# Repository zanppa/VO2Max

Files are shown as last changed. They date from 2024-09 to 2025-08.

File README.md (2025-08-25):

# Vo2max
A portable and affordable DIY [spirometer](https://en.wikipedia.org/wiki/Spirometer) project to measure [VO2 Max](https://en.wikipedia.org/wiki/VO2_max) during an excercise. This is still a prototype and heavily in development.

This project turned out to be a complete rewrite and redesign of [Ivor Hewitt's VO2max](https://github.com/ihewitt/VO2max) spirometer project, which in turn was based on [Rabbitcreek's project](https://www.instructables.com/Accurate-VO2-Max-for-Zwift-and-Strava/).

The main idea was to have a fully 3D printable system, but printing the mask part turned out to be difficult so the current version uses parts from a commercial (but affordable) mask. There are plans to develop a model that can be 3D printed with soft material (TPU/TPE).

Current features:
 - [X] Exhalation volume measurement (with calibration function)
 - [X] Exhalation oxygen level measurement (with calibration function)
 - [X] VE and VO2(max) calculations
 - [X] Ambient pressure and temperature measurement for reducing measurements to STDP 
 - [X] Bluetooth LE heart rate sensor support
 - [X] Streaming data over WiFi to computer
 - [X] PC companion program to monitor and record the WiFi stream
 - [X] Recording values to memory buffer (1024 samples, at 15 s calculation interval over 4 hours)
 - [X] Storing recorded values to a file (single file in flash, retained over power off)
 - [X] PC tool to read and store the recorded values
 - [ ] Bluetooth [Golden Cheetah](https://www.goldencheetah.org/) support as VO2 Master (based on Ihewitt's code)
 
Main architectural changes in the code:
 - Restructured to use FreeRTOS tasks
 - Time-accurate sampling of sensors, e.g. air flow is measured every 20 ms
 - Lower priority tasks like bluetooth, wifi and display do not interrupt sensor reading
 - Code is divided to "sub modules" for easier upkeep
 
## Usage
This VO2Max measurement device is designed to have two operation modes:

1. Stand-alone use. In this mode the device is used independently and handles all calculations internally. Values can be monitored from the device's display, and the data is stored to memory (and optionally to flash memory). The stored values can later be transferred to a computer via WiFi.
2. Real-time monitoring mode. In this mode a computer is connected to the device via WiFi and all measured quantities are transferred to the computer in real time. The computer can record the values and/or do the calculations (of course, also the VO2Max's calculated values are transferred).

For detailed usage info see [how-to-use.md](how-to-use.md).

## Hardware
This is a listing of the hardware that is used and supported by the code and 3D models. Some of the hardware were different from the reference projects for availability reasons in the EU, or due to technical reasons like mounting.

 - A rubber (silicone?) half face dust mask with detachable parts, see links/pictures below
 - [LilyGo T-Display](https://www.lilygo.cc/products/lilygo%C2%AE-ttgo-t-display-1-14-inch-lcd-esp32-control-board) ESP32 development board with 1.14" display
 - [DFRobot SEN0322](https://www.dfrobot.com/product-2052.html) Gravity: Electrochemical Oxygen sensor (0-25% Vol, I2C)
 - [Sensirion SDP801](https://sensirion.com/products/catalog/SDP801-500Pa/) Digital +/-500Pa differential pressure sensor, I2C, manifold connection
 - [Bosch BMP388](https://www.bosch-sensortec.com/products/environmental-sensors/pressure-sensors/bmp388/) ambient pressure sensor (e.g. [DFRobot SEN0251 Gravity: BMP388](https://www.dfrobot.com/product-1792.html))
 - Thread forming 2.5x8mm screws (6 pcs) (e.g. [Bossard 3034065](https://www.bossard.com/eshop/global-en/direct-assembly-screws/direct-assembly-screws-for-plastics/ecosyn-plast/p/82428/?category=01.200.300&index=7)) and 2.5x16mm screws (2 pcs) (e.g. [Bossard 3034077](https://www.bossard.com/eshop/global-en/direct-assembly-screws/direct-assembly-screws-for-plastics/ecosyn-plast/p/82428/?category=01.200.300&index=7))
 - 14500 size Lithium-ion battery and suitable connection parts (spring terminals or similar)
 - 2 pcs of 4.5 x 1.5 mm O-rings
 
## Where to buy
Most of the necessary electronics components were bought from [Mouser](https://eu.mouser.com/).

The display and half mask was bought from [Aliexpress](https://www.aliexpress.com). Many stores had similar masks so a random, somewhat professional looking one was selected and the mask that was received was ok. Prepare for a long delivery time, 6 weeks or so.

Links to the main components that were used are below with their price at the time of building (incl. VAT etc.).

| Component | Source | Price |
| --------- | ------ | ----- |
| DFRobot Sen0322 | [Mouser](https://eu.mouser.com/ProductDetail/DFRobot/SEN0322?qs=sPbYRqrBIVnCRTCgFw%2FJyQ%3D%3D) | 50.13 € |
| Sensirion SDP801 | [Mouser](https://eu.mouser.com/ProductDetail/Sensirion/SDP801-500Pa?qs=PzGy0jfpSMsYh%2Fiz3%252Braew%3D%3D) | 30.50 € |
| DFRobot SEN0251 BMP388 | [Mouser](https://eu.mouser.com/ProductDetail/DFRobot/SEN0251?qs=sGAEpiMZZMsvmS05OVPORkos2oZHucfRYva4AowfgwtRmiD%2F%252BmISIg%3D%3D) | 6.42 € |
| Lilygo T-Display 16MB CH9102F | [Aliexpress lilygo Official store](https://www.aliexpress.com/item/33048962331.html) | 16.18 € |
| Dustproof half-mask | [Aliepress CKE-Labour Pro Store](https://www.aliexpress.com/item/1005005820042955.html) | $ 6.24 |

# Assembly

## Valve assembly
Exhalation and inhalation valves are required. Valve itself consists of two 3D printed parts (body and membrane holder), membrane template and the membrane itself. In addition, inhalation valve needs a counterpart for mounting. Current design uses two different sizes of valves due to how the commercial mask was built.

 1. Print all the valve parts
 2. Using the template, cut the membrane from suitable material. Rubber glove can be used as the membrane. One may experiment with different materials
 3. Insert the membrane into the valve body
 4. Place the membrane holder on the membrane. Carefully push the ends of the holder slightly and rotate the holder into the clips. Take care to ensure that the membrane is still centered and has no wrinkles
 
## I2C distribution board
A simple I2C distribution board is needed to be mounted on top of the Sensirion SDP801 sensor. This also helps in mounting the sensor.

Mill or etch and drill or order the board, and then solder the sensor wires to them. I recommend measuring the wires yourself but the lengths of the wires are roughly:
 - 20 cm for the oxygen sensor
 - 16 cm for the ambient pressure sensor
 - TBD cm for the display/processor
 
I recommend routing one sensor wire from the backside and other wires from the front.

Also solder 1.3 kOhm pull-up resistors between VDD and SDA and SCL.

Finally the Sensirion SDP801 can be soldered to the distribution board.

## Main body assembly
Main body consists of a single 3D-printed main part. Support is needed at the bottom parts and about 6 mm outer brim should be used to ensure that the part stays upright. With a bed-slinger printer, orient the print so that the wide side is parallel to the moving axis.

 1. Print the body and remove all support material
 2. Mount the oxygen sensor on top with 4x 2.5x8mm screws
 3. Mount the ambient pressure/temperature sensor on the side with 2x 8mm screws
 4. Place the O-rings on the recesses of the pressure sensor location
 5. Mount the SDP801 pressure sensor with 2x 2.5x16mm screws
 6. Wire the battery terminals to the T-display battery connector
 7. Install the battery terminals and connect the connector to T-display
 6. Place the display on the front of the unit
 7. Carefully measure cables, cut and solder them, removing parts from the body if necessary during soldering
 8. Use 1.3 kOhm external pull-up resistors for I2C SDA and SCL (preferably soldered to the I2C distribution board)

Note that the battery terminals nor the power switch are currently included in the model. One should find suitable parts for this and glue them in place.

The battery holder might be a bit tight, so some sanding/cutting of the edges may be necessary.
 
## Flashing the firmware
The firmware was built with PlatformIO v core 6.1.18, home 3.4.4. One needs to install lilygo-t-display board (or it may get installed automatically when building...)

Following external libraries are needed:

 - TFT_eSPI (version 2.5.34)
 - NimBLE-Arduino for Bluetooth LE (version 1.4.1)
 
Other drivers are included in the repository with necessary modifications.

To build the software select following as the board settings:

 * Board: Lilygo-t-display
 * Upload Speed: 921600
 * CPU Frequency: 240Mhz (WiFi/BT)
 * Flash Frequency: 80Mhz
 * Flash Mode: QIO
 * Partition Scheme: Default.csv [4MB with spiffs (1.2MB APP/1.5 SPIFFS)]
 * Core Debug Level: None --> For debugging can set also different values, for release select None
 * PSRAM: No

# Disclaimer
This is not a medical device! Use at your own responsibility.

This repository contains code, models and similar for educational purposes only and are supposed 
to be used for reference. Everything is provided as is, without any warranty. The author is not 
liable for any damages or other liability arising from use of anything provided here.

# Copyright
Copyright 2024, 2025 Lauri Peltonen

Licensed under GPLv3.

Drivers included in this repository may have their own licenses which are included in the relevant 
source files.

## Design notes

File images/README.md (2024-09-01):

This directory contains images and pictures of the VO2Max device

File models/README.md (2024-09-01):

This directory contains the 3D models that need to be 3D printed.

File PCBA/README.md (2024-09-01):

# Sensirion SDP801 PCBA
This directory contains the simple PCBA to be mounted on top of the Sensirion SDP801 
pressure sensor. It also functions as a I2C distribution board.

Gerbers are provided for reference, as the board is very simple and was drawn 
by hand.

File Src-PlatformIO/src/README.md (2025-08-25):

# Source code for VO2Max project
This directory contains the source code for the VO2Max project.

Source code is written for ESP32 with PlatformIO (Core 6.1.18, Home 3.4.4).

## PlatformIO board settings
The settings are defined in ```platformio.ini``` but the key values are listed here also.

 * Board: Lilygo-t-display
 * Upload Speed: 921600
 * CPU Frequency: 240Mhz (WiFi/BT)
 * Flash Frequency: 80Mhz
 * Flash Mode: QIO
 * Partition Scheme: Default.csv [4MB with spiffs (1.2MB APP/1.5 SPIFFS)]
 * Core Debug Level: None --> For debugging can set also different values, for release select None
 * PSRAM: No

## External library requrirements
 * TFT_eSPI (tested with version 2.5.34)
 * NimBLE_Arduino (tested with version 1.4.1)

## Other stuff
Remember to modify the TFT_eSPI configuration file to select T-Display! File should be located in ```.pio/libdeps/lilygo-t-display/TFT_eSPI/User_Setup_Select.h```. The correct line to uncomment is 
```
#include <User_Setups/Setup25_TTGO_T_Display.h>    // Setup file for ESP32 and TTGO T-Display ST7789V SPI bus TFT
```

Don't forget to comment out the default custom ```User_Setup.h``` configuration file
```
//#include <User_Setup.h>           // Default setup is root library folder
```

With NimBLE-Arduino the code just barely fits into default partition (1.25 MB App, 1.375 MB SPIFFS).

It would be possible to change to huge_app (3 MB app, 0.875 MB SPIFFS) if more application space is needed.

## Library requirements
### External
 * TFT_eSPI @ 2.5.43
 * NimBLE-Arduino @ 1.4.1

### Built into ESP32 platform
 * EEPROM @ 2.0.0
 * ESP32 Async UDP @ 2.0.0
 * WiFi @ 2.0.0

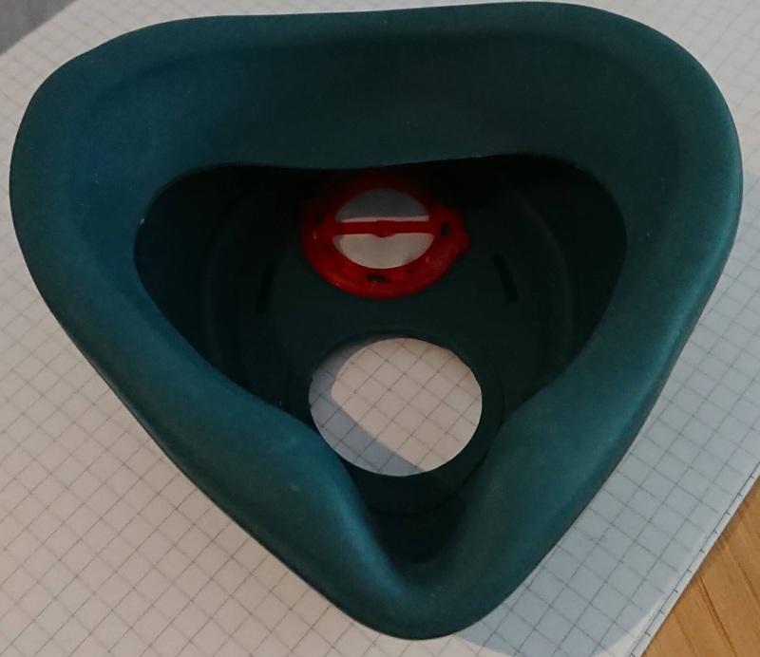
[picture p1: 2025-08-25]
images/inlet_3.jpg

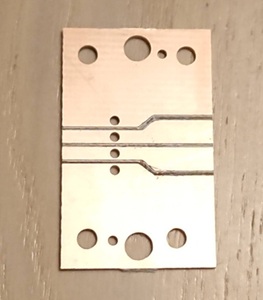
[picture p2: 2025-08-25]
images/i2c_board_1.jpg

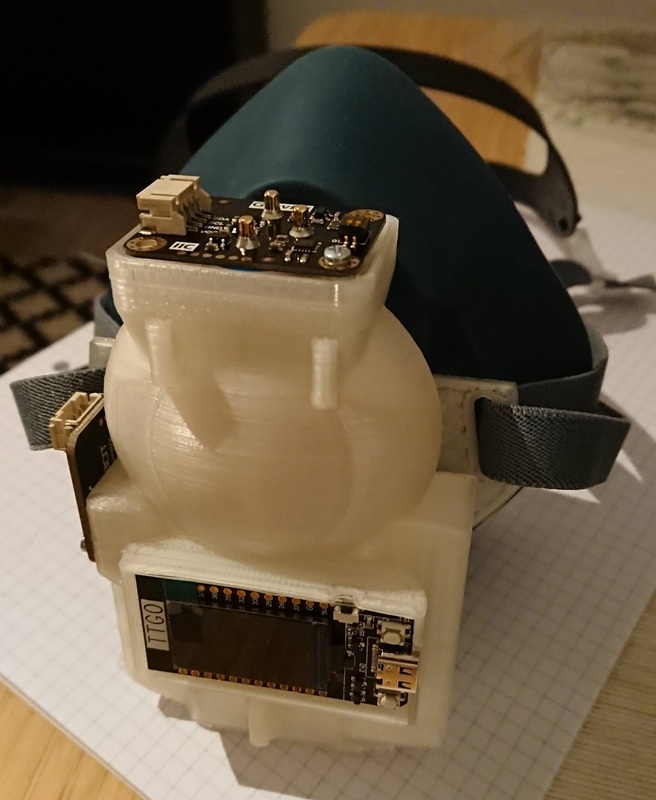
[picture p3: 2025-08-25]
images/boards_1.jpg

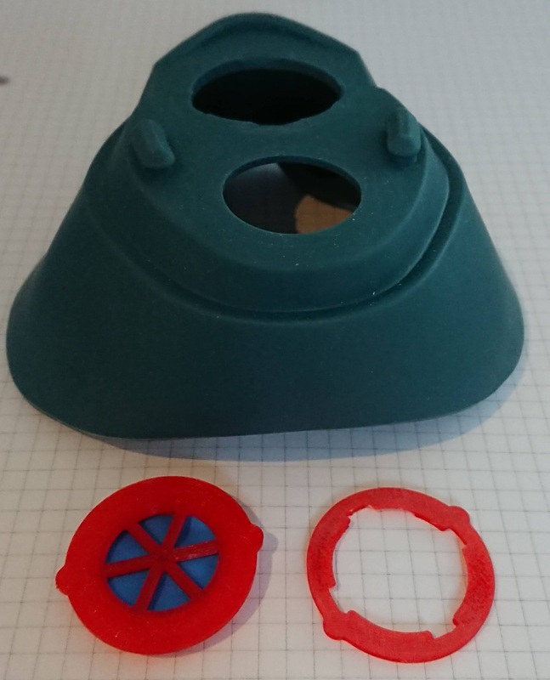
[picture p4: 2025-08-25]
images/inlet_1.jpg

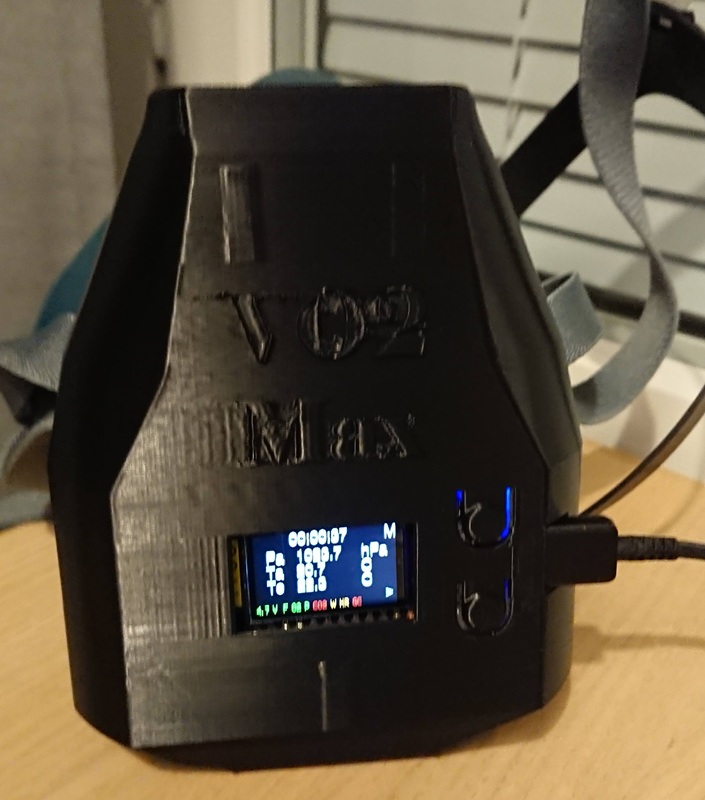
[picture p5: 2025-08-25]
images/cover_1.jpg

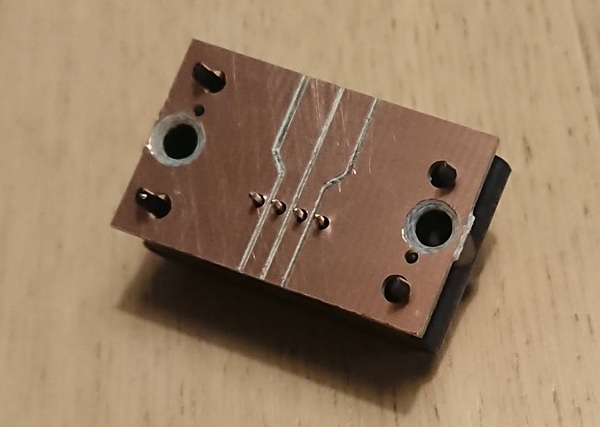
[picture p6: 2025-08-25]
images/i2c_board_2.jpg

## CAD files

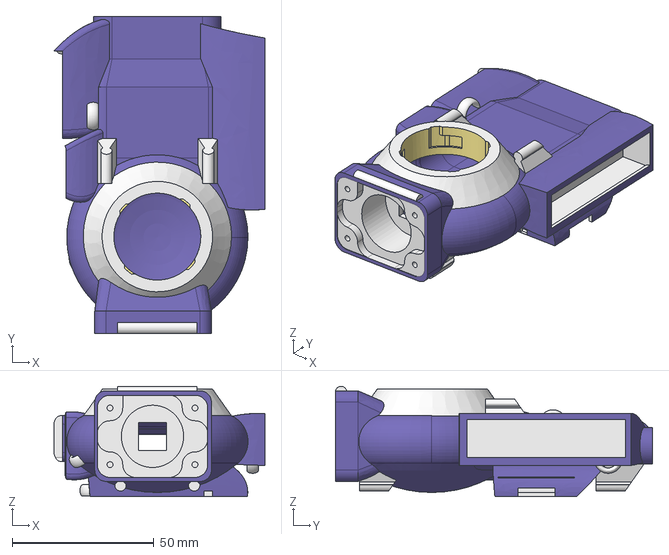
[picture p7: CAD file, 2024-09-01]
models/Main model v12.step
74.5 x 112.0 x 39.0 mm

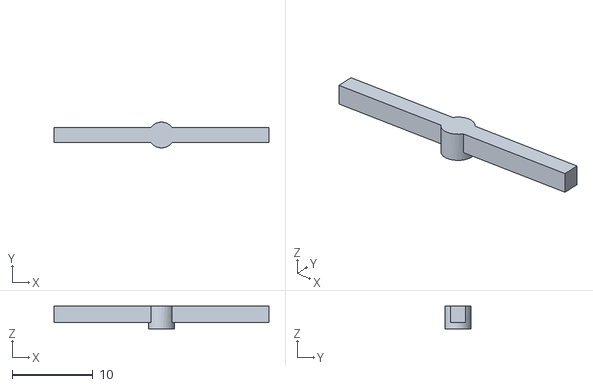
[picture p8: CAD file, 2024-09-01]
models/Outlet valve v2 30mm membrane holder.stl
26.6 x 3.20 x 2.80

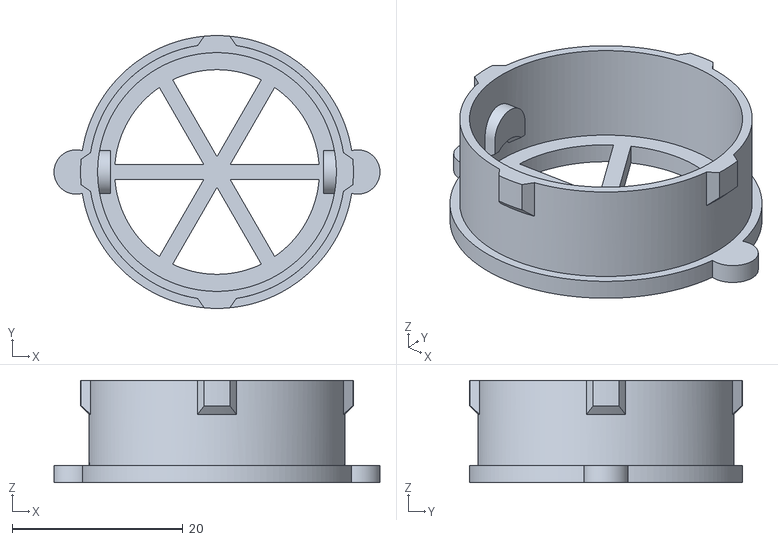
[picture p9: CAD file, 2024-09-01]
models/Outlet valve v2 30mm body.stl
38.2 x 32.0 x 12.0

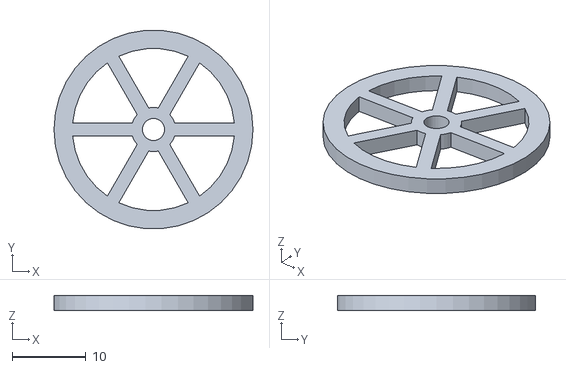
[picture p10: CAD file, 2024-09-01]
models/Outlet valve v1 30mm template.stl
27.0 x 26.9 x 2.00

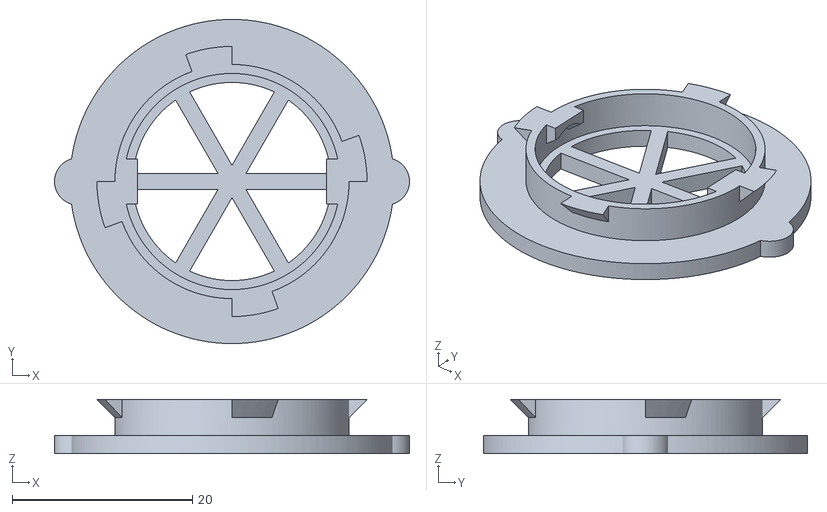
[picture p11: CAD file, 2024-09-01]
models/Inlet valve v4 26mm body.stl
39.4 x 36.0 x 6.00

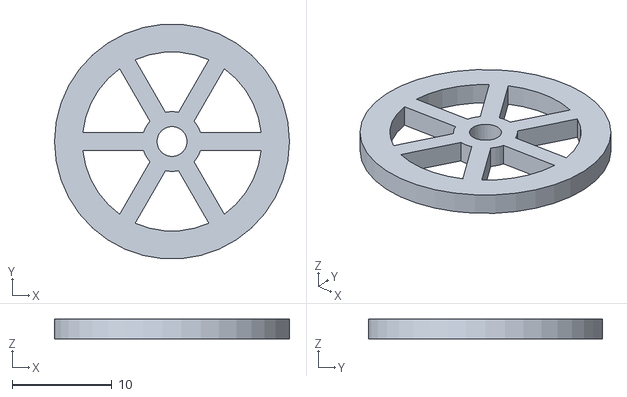
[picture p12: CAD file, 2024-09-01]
models/Inlet valve v3 26mm template.stl
23.6 x 23.5 x 2.00

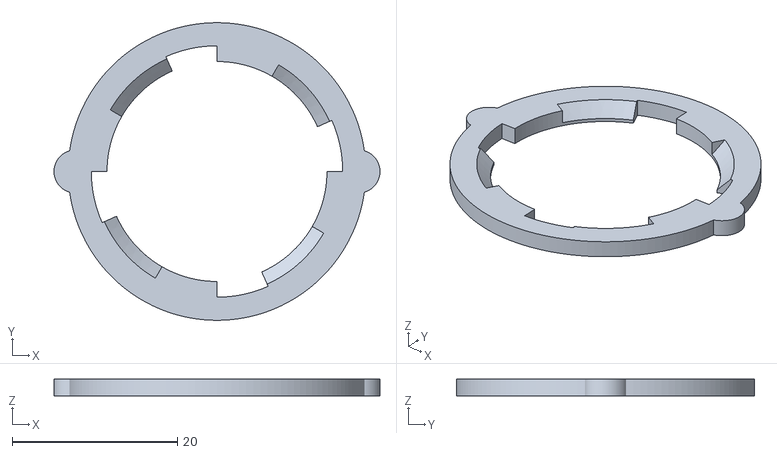
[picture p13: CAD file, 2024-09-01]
models/Inlet valve v4 26mm retainer.stl
39.4 x 36.0 x 2.00

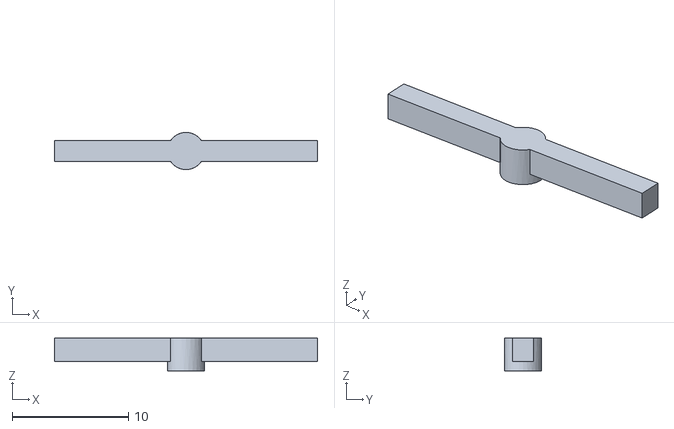
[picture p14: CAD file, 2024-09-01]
models/Inlet valve v3 26mm membrane holder.stl
22.6 x 3.20 x 2.80

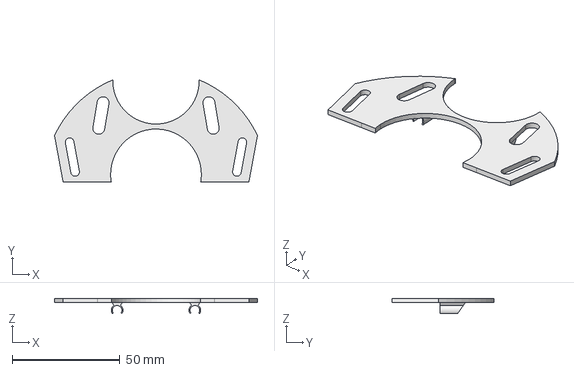
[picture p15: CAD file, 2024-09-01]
models/Mask holder v10.step
94.0 x 47.4 x 7.05 mm

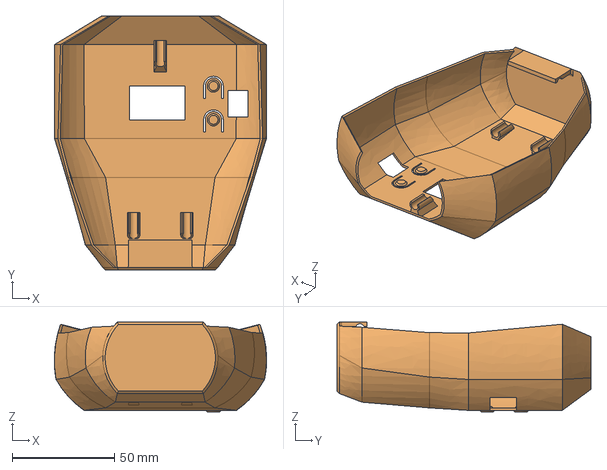
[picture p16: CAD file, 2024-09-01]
models/Cover v12.step
103.8 x 124.2 x 44.0 mm

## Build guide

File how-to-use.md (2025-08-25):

# How to use VO2Max
This document describes basic usage of the VO2Max portable spirometer.

## Getting started

The device is powered on either by plugging in USB-C cable or by connecting a Li-Ion battery to the T-Display board.

After power on, the oxygen sensor requires 3 minutes of warm-up for measurement to be stable and accurate. A timer will be shown on the display counting down from 180 every second and displaying the oxygen sensor reading. This screen can be skipped if device has been previously running. After the time has passed or the wait was skipped, the oxygen sensor reading will be used as initial base-level oxygen contentration. For this reason, the sensor should be vented with fresh air if rebooted (do NOT blow into the sensor/mask as exhale air has low oxygen contenration!).

A default status screen will be shown. In the status screen top row shows currently elapsed time. Then values (depending on the selected status screen) will be shown, like VO2 value and heart rate, or like in example below, ambient pressure and temperature and exhale temperature.

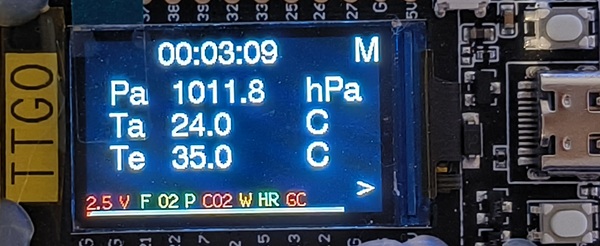
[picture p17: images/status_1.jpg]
Status screen


On the bottom of the status screen a list of symbols show the status of the device:

| Symbol | Description |
|--------|-------------|
| 2.5V  | Battery voltage. If USB cable is connected, charging supply voltage. Color indicates state: Blue=charger connected, green=full, yellow=normal, red=low |
| F      | Air flow (pressure) sensor status. Green=ok, red=error/disabled |
| O2     | Oxygen sensor status. Green=ok, red=error/disabled |
| P      | Ambient pressure sensor status. Green=ok, red=error/disabled |
| CO2    | CO2 sensor status. Green=ok, red=error/disabled |
| W      | Wifi status. Green=wifi on & client(s) connected, yellow=wifi on (no clients), red=off/error |
| HR     | BLE Heart rate sensor status. Green=enabled & connected, yellow=enabled (not connected), red=disabled/error |
| GC     | Golden cheetah status. Green=enabled & connected, yellow=enabled (not connected), red=disabled/error |

The final line on the status screen shows internal data storage buffer status. Red means used memory, while grey means free memory. The line slowly fills with red until the buffer is full and oldest data will get overwritten.

The T-Display has two buttons on the right side. The top one, labeled ```M``` enters the menu while the bottom one (```>```) changes the status screen. On the top there is a small reset button which resets the processor.

## Using the menu

Menu is opened by pressing the top (```M```) button while in status screen. In the menu the top button (```>```) selects the currently highlighted menu item while the bottom button (```V```) moves to the next menu item. When reaching the last item, the bottom button jumps back to the first menu item. The menu structure is described below.

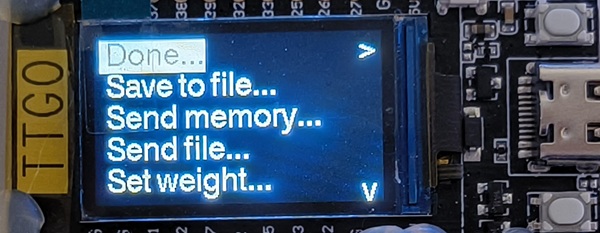
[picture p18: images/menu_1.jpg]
Menu 1st page


| Menu item | Description |
|-----------|-------------|
| Done... | Close the menu and apply & save any changes. Settings will be stored and remembered over reboot |
| Save to file... | Save the storage buffer (all the recorded values) to flash memory |
| Send memory... | Send the recorded memory buffer over WiFi to a computer |
| Send file... | Send the saved record file to a computer over WiFi |
| Set weight... | Set the user's weight in kg |
| Interval [15s] | Set the calculation interval (shows the value in brackets). Possible values: 5s, 10s, 15s, 30s, 60s. Default 15s |
| Store rate [All] | Set the memory storage rate. Options: All=store every calculation result, 1:2=store every other calculation result, 1:3=store one third, 1:5=store one fifth, 1:10=store every tenth. Default All |
| Recalibrate O2... | Trigger O2 sensor recalibration. Must be done when the sensor has been in fresh air for a long time. Expected to see 20.93 % oxygen concentration when calibrating |
| Calibrate flow... | Calibrate the flow sensor. First asks for the calibration syringe volume and then prompts user to empty the syringe through the mask. Flow sensor correction factor will be applied based on the difference between measured and expected volumes |
| Wifi [Yes] | Enable or disable Wifi. Options Yes=enable, No=disable |
| Wifi name... | Set the Wifi network name that will be created by VO2Max |
| Wifi password... | Set the Wifi network password |
| CO2 sensor [No] | Use CO2 sensor. Options Yes=Use the CO2 sensor, No=don't use CO2 sensor |
| G Cheetah [No] | Enable Golden Cheetah bluetooth feature. Options Yes=enable, No=disable |
| HR sensor [Yes] | Enable use of Bluetooth LE heart rate sensor. Options Yes=enable, No=disable |
| HR scan... | Scan for Bluetooth LE heart rate sensors. Scans for about 10 seconds and connects to the first heart rate sensor found, if any. The sensor (address) will be stored and connected automatically when powering up |
| Start over... | Reset all calculations, storage memory and elapsed time |

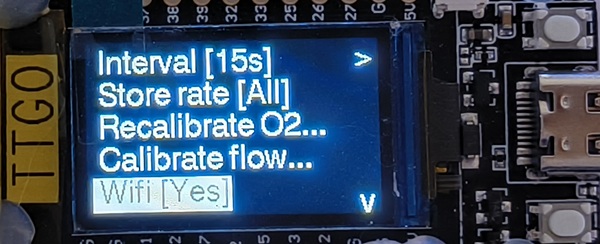
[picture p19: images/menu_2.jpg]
Menu 2nd page


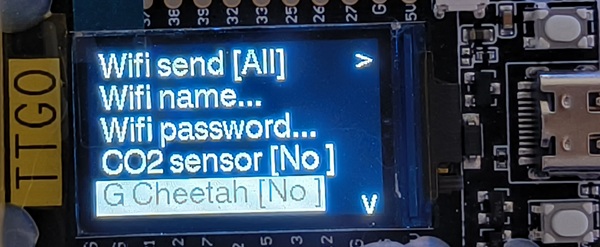
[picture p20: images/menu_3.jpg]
Menu 3rd page


Notes:
 - When selecting menu item with discrete set of options, the select button (top, ```>```) selects the next option. From the last option, the selection returns to the first
 - When entering numbers (like weight), top button (```+```) increases the value and bottom button (```-```)decreases. Waiting for 5 seconds without pressing any buttons accepts the value\
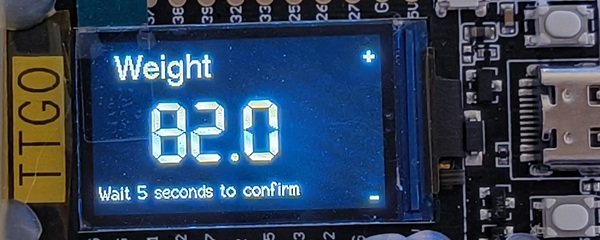
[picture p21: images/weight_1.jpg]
Setting a number

 - When entering text (like Wifi name), top button (```>```) goes to next character and bottom button (```V```) changes the currently selected character. Waiting for 5 seconds without pressing any buttons accepts the value
 - Heart rate sensor scanning looks like following:\
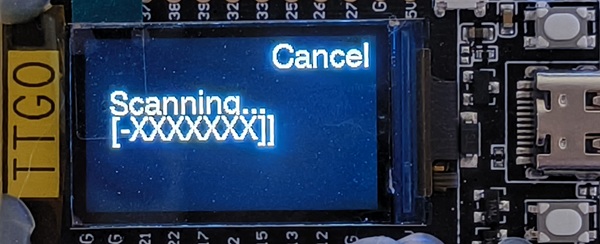
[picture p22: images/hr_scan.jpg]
HR sensor scanning
\
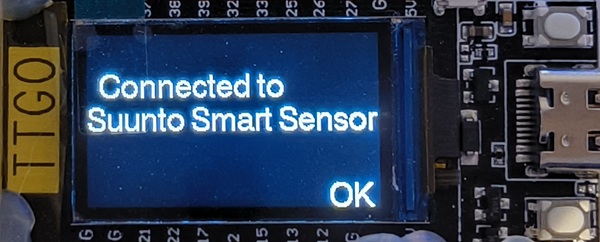
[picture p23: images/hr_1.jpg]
HR sensor found


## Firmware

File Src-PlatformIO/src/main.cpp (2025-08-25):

/*
 * VO2 sensor for measuring VO2 and VO2max during exercise
 *
 * Copyright (C) 2024, 2025 Lauri Peltonen
 * GPL V3
 *
 * Based heavily on IHewitt's VO2max project
 * https://github.com/ihewitt/VO2max
 *
 *
 * Main parts:
 *   Lilygo T-display (ESP32, 1.14" display, bluetooth, wifi)
 *   DFRobot SEN0322 I2C oxygen sensor
 *   Sensirion SDP801 500 Pa I2C differential pressure sensor
 *   BMP388 ambient pressure sensor (DFRobot Gravity BMP388)
 *
 *
 * PlatformIO board settings:
 *
 * Board: Lilygo-t-display
 * Upload Speed: 921600
 * CPU Frequency: 240Mhz (WiFi/BT)
 * Flash Frequency: 80Mhz
 * Flash Mode: QIO
 * Partition Scheme: Default.csv [4MB with spiffs (1.2MB APP/1.5 SPIFFS)]
 * Core Debug Level: None --> For debugging can set also different values, for release select None
 * PSRAM: No
 *
 * Remember to modify the TFT_eSPI configuration file to select T-Display!
 * Select this one line in "user_setup_select.h"
 * #include <User_Setups/Setup25_TTGO_T_Display.h>    // Setup file for ESP32 and TTGO T-Display ST7789V SPI bus TFT
 * and don't forget to comment out the custom user setup
 * //#include <User_Setup.h>           // Default setup is root library folder
 * 
 * 
 * With NimBLE-Arduino the code just barely fits into default partition.
 * In case of problems (e.g. if program does not fit with debug level = info), one can use
 *    huge_app.csv / Huge APP (3 MB No OTA / 1 MB SPIFFS)
 * partition scheme to make the program fit.
 *
 */

/*
 * External boards requirements
 *  - esp32 by Espressif (3.0.2 --> 3.0.5)
 *
 * External library requirements
 * - tft_espi (version 2.5.43)
 * - NimBLE_Arduino (version 1.4.1)
 */


#include <freertos/FreeRTOS.h>
#include <freertos/task.h>

//#include "driver/adc.h"
#include "esp_adc_cal.h"
#include "driver/gpio.h"

#include <TFT_eSPI.h>

#include "Preferences.h"

#include "config.h"
#include "sensorTask.h"
#include "buttonsTask.h"
#include "wifiTask.h"
#include "status.h"
#include "menu.h"
#include "BLE_HRBelt.h"
#include "files.h"


#define VO2_PIN_DEBUG   27
#define VO2_PIN_ADC_EN  14
#define VO2_PIN_BAT_VOLT  34

// Custom, hand fit gain and offset values from ADC reading to battery voltage
#define ADC_CUSTOM_GAIN   2.89
#define ADC_CUSTOM_OFFSET 0.546

#define PREFS_STORE_SIZE   sizeof(settings_t)
Preferences preferences;    // To store configuration values to NVS (non-volatile storage) (instead of flash)

// Default settings
settings_t global_settings = {
  .flowCorrectionFactor = 1.0,
  .userWeight = 80.0,
  .wifiDataRate = 0,
  .integrationTime = 15000,
  .hrsensor_enable = false,
  .co2sensor_enable = false,
  .wifi_enable = true,
  .cheetah_enable = false,
  .HRSensorAddress = {0, 0, 0, 0, 0, 0},
  .wifiStationName = {'V', 'O', '2', 'M', 'A', 'X', '_', 0},
  .wifiPassword = {'4', '3', '2', '1', 'a', 's', 'd', 'f', 0},
};


#define PRIORITY_SENSORTASK   50
#define PRIORITY_WIFITASK     20
#define PRIORITY_BLETASK      15
#define PRIORITY_BUTTONTASK   10
#define PRIORITY_GUITASK      5

// Display
TFT_eSPI tft;

static const char *TAG_VO2 = "VO2MAX";

// Handles to other tasks
TaskHandle_t task_sensorTask;
TaskHandle_t task_buttonTask;
TaskHandle_t task_wifiTask;
//TaskHandle_t task_guiTask;
TaskHandle_t task_BLETask;
TimerHandle_t timer_clock;

volatile uint32_t seconds_from_start = 0;

void debugPrintConfig(void)
{
  Serial.println("Configuration:");
  Serial.print(" Correction factor: ");
  Serial.println(global_settings.flowCorrectionFactor);
  Serial.print(" Weight: ");
  Serial.println(global_settings.userWeight);
  Serial.print(" Wifi rate: ");
  Serial.println(global_settings.wifiDataRate);
  Serial.print(" Int time: ");
  Serial.println(global_settings.integrationTime);
  Serial.print(" Store rate: ");
  Serial.println(global_settings.storeDataRate);
  Serial.print(" HR Sensor: ");
  Serial.println(global_settings.hrsensor_enable);
  Serial.print(" CO2 sensor: ");
  Serial.println(global_settings.co2sensor_enable);
  Serial.print(" Wifi: ");
  Serial.println(global_settings.wifi_enable);
  Serial.print(" Wifi AP name: ");
  Serial.println(global_settings.wifiStationName);
  Serial.print(" Golden Cheetah: ");
  Serial.println(global_settings.cheetah_enable);
  Serial.print(" HR Address: ");
  for(int i=0;i<6;i++)
    Serial.print(global_settings.HRSensorAddress[i], HEX);
  Serial.println();
}

// Keep track of running time in nice units
void clockTimer(TimerHandle_t xTimer)
{
  seconds_from_start++;
}

uint16_t battery_raw = 0.0;
float battery_voltage = 0.0;
float vref_scale = 1.0;

float readBatteryVoltage()
{
  digitalWrite(VO2_PIN_ADC_EN, HIGH);
  vTaskDelay(pdMS_TO_TICKS(10));
  battery_raw = analogRead(VO2_PIN_BAT_VOLT);
  float measurement = (float)battery_raw;
  measurement = (measurement / 4095.0) * vref_scale * 2;    // vref = internal ADC reference, 2 = resistor division
  measurement = (measurement * ADC_CUSTOM_GAIN) + ADC_CUSTOM_OFFSET; // Custom linear fit from ADC to voltage
  digitalWrite(VO2_PIN_ADC_EN, LOW);
  battery_voltage = measurement;

  //ESP_LOGD(TAG_VO2, "Battery raw %d", battery_raw);
  //ESP_LOGD(TAG_VO2, "Battery scaled %f V", measurement);

  return measurement;
}

// Load settings structure from NVS
bool loadSettings() {
  uint8_t b;
  settings_t new_settings;

  if(!preferences.begin("vo2max", true)) {  // Open NVS namespace for reading
    ESP_LOGI(TAG_VO2, "Preferences: No previous preferences stored.");
    preferences.end();
    return false;
  }

  // Check magic and version to make sure NVS contents are compatible
  if(!preferences.isKey("magic") || (b = preferences.getUChar("magic", 0)) != SETTINGS_MAGIC) {
    ESP_LOGE(TAG_VO2, "Preferences: Magic does not match (%x != %x)", b, SETTINGS_MAGIC);
    preferences.end();
    return false;
  }
  if(!preferences.isKey("version") || (b = preferences.getUChar("version", 0)) != SETTINGS_VERSION) {
    ESP_LOGE(TAG_VO2, "Preferences: Version does not match (%d != %d)", b, SETTINGS_VERSION);
    preferences.end();
    return false;
  }

  if(!preferences.isKey("prefs")) {
    ESP_LOGE(TAG_VO2, "Preferences: prefs key not found");
    preferences.end();
    return false;
  }

  if((b = preferences.getBytesLength("prefs")) != PREFS_STORE_SIZE) {
    ESP_LOGE(TAG_VO2, "Preferences: prefs data length not correct (%d != %d)", b, PREFS_STORE_SIZE);
    preferences.end();
    return false;
  }

  // Read the settings to temporary array
  if(preferences.getBytes("prefs", (void *)&new_settings, PREFS_STORE_SIZE) != PREFS_STORE_SIZE) {
    ESP_LOGE(TAG_VO2, "Preferences: Failed to load preference values!");
    preferences.end();
    return false;
  }

  // Data should be succesfully restored, copy them to the correct array
  memcpy(&global_settings, &new_settings, PREFS_STORE_SIZE);

  ESP_LOGI(TAG_VO2, "Preferences: Settings restored");

  preferences.end();
  return true;
}

// Store current settings struct to NVS
void storeSettings() {
  bool success = false;

  ESP_LOGI(TAG_VO2, "Preferences: Storing settings");

  if(!preferences.begin("vo2max", false)) { // Open NVS namespace for read and write
    ESP_LOGE(TAG_VO2, "Preferences: Namespace creation failed");
    preferences.end();
    return;
  }
  if(preferences.putBytes("prefs", (void *)&global_settings, PREFS_STORE_SIZE) != PREFS_STORE_SIZE) {
    ESP_LOGE(TAG_VO2, "Preferences: Could not write preferences");
    preferences.end();
    return;
  }
  if(!preferences.putUChar("magic", SETTINGS_MAGIC)) {
    ESP_LOGE(TAG_VO2, "Preferences: Could not write magic");
    preferences.end();
    return;
  }
  if(!preferences.putUChar("version", SETTINGS_VERSION)) {
    ESP_LOGE(TAG_VO2, "Preferences: Could not write version");
    preferences.end();
    return;
  }
  
  ESP_LOGI(TAG_VO2, "Preferences: Settings stored");
  ESP_LOGD(TAG_VO2, "Preferences: %d entries free", preferences.freeEntries());
  preferences.end();
}


void setup() {
  // Initialize serial so we get debug messages etc.
  Serial.begin(115200);

  // Pre-initialize button I/O pins so we can control the boot-up if necessary
  pinMode(BUTTON_1_PIN, INPUT_PULLUP);
  pinMode(BUTTON_2_PIN, INPUT_PULLUP);

  // Debug print default config
  // debugPrintConfig();

  // If upper button is held down during boot, reset to default settings,
  // i.e. do not read from NVS
  if(digitalRead(BUTTON_2_PIN)) // Returns true if button is not pressed
    loadSettings();
  else 
    ESP_LOGI(TAG_VO2, "Setup: Reverting to default settings");

  // Debug print loaded config
  debugPrintConfig();

  // Initialize the display
  tft.init();
  tft.setRotation(1);
  tft.fillScreen(TFT_BLACK);
  //tft.setTextColor(TFT_LIGHTGREY, TFT_BLACK);
  //tft.setCursor(24, 48, 7);
  //tft.print("VO2Max");

  pinMode(VO2_PIN_DEBUG, OUTPUT); // DEBUG output pin

  // Setup ADC  for battery voltage measurement
  esp_adc_cal_characteristics_t adc_chars;
  esp_adc_cal_value_t val_type = esp_adc_cal_characterize((adc_unit_t)ADC_UNIT_1, (adc_atten_t)ADC_ATTEN_DB_11, (adc_bits_width_t)ADC_WIDTH_BIT_12, 1100, &adc_chars);
  ESP_LOGD(TAG_VO2, "Battery reference %d", adc_chars.vref);
  adc_attenuation_t attenuation = ADC_11db; // 11 dB can measure max 3.1 V
  analogSetAttenuation(attenuation);  // Set generic attenuation as we only use ADC for battery
  vref_scale = (float)adc_chars.vref / 1000.0;  // 4095 (100 % of scale) equals to vref so this is the scaling value
  //pinMode(VO2_PIN_BAT_VOLT, INPUT);

  pinMode(VO2_PIN_ADC_EN, OUTPUT);
  digitalWrite(VO2_PIN_ADC_EN, LOW);

  // Initialize status screens
  initScreens();

  // Initialize button interrupt, one way to handle buttons
  buttonInit();
  attachInterrupt(BUTTON_1_PIN, buttonInterrupt, CHANGE);
  attachInterrupt(BUTTON_2_PIN, buttonInterrupt, CHANGE);

  // Initialize filesystem for storage
  init_filesystem();

  // Create other tasks
  xTaskCreate(sensorTask, "sensor", 4096, nullptr, PRIORITY_SENSORTASK, &task_sensorTask);
  sensorWaitEvent(SENSOR_INIT_DONE, pdMS_TO_TICKS(1000));

  //xTaskCreate(buttonTask, "buttons", 1024, nullptr, PRIORITY_BUTTONTASK, &task_buttonTask); // Alternative way to handle buttons
  xTaskCreate(wifiTask, "wifi", 4096, nullptr, PRIORITY_WIFITASK, &task_wifiTask);
  xTaskCreate(BLETask, "BLE", 4096, nullptr, PRIORITY_BLETASK, &task_BLETask);

  timer_clock = xTimerCreate("clock", pdMS_TO_TICKS(1000), pdTRUE, nullptr, clockTimer);
  xTimerStart(timer_clock, 0);

  // Update initial configuration, default or from NVS
  sensorSetConfiguration();

  // Queue automatic start of other features that may also be disabled
  if(global_settings.hrsensor_enable)
    BLEHRConnect();

  if(global_settings.cheetah_enable)
    BLEGCStart();

  if(global_settings.wifi_enable)
    wifiRequestStart();
}

static sensorData_t temp_daatta;
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

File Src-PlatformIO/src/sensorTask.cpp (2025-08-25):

/*
 * Main sensor task for VO2 sensor
 * Reads flow with pressure sensor, oxygen concentration
 * and ambient pressure & temperature
 * and handles all integrations and calculations
 *
 *
 * Copyright (C) 2024 Lauri Peltonen
 * GPL V3
 *
 * Volume compensation equations from
 * https://sites.uni.edu/dolgener/Instrumentation/Repeating%20material/VO2%20Computation.pdf
 *
 * Venturi calculation for flow rate from https://en.wikipedia.org/wiki/Venturi_effect
 * Air density calculation from https://en.wikipedia.org/wiki/Density_of_air
 */

#include <freertos/FreeRTOS.h>
#include <freertos/task.h>
#include <freertos/event_groups.h>

#include "esp_log.h"

#include <Arduino.h> // DEBUG

#include <math.h>

#include "config.h"

#include "sensorTask.h"

#include "sdpsensor.h"
#include "bmp388sensor.h"
#include "DFRobot_OxygenSensor.h"

const char *TAG_SENSOR = "sensorTask";

#define I2C_DEFAULT_TIMEOUT   (320000)  // time = this * APB 80 MHz clock. 80 000 = 1 ms

esp_err_t initialize_I2C(i2c_port_t i2c_port=I2C_PORT, int pinSDA=21, int pinSCL=22);
esp_err_t reset_I2C();

// Sensor definitions
SDPSensor flow_sensor(0x26, I2C_PORT);    // SDP801-500Pa has address of 0x26
BMP388Sensor pressure_sensor(0x77, I2C_PORT); // BMP388 atmospheric pressure sensor (address selected 0x77, other setting is 0x76)
O2Sensor oxygen_sensor(0x73, I2C_PORT);   // DFRobot Sen0322 oxygen sensor (my was default 0x73 with both address pins "low")


// TODO: Move to config?
#define READINTERVAL    10    // ms, how often we run the sensor reading task
#define FLOWINTERVAL    (2*READINTERVAL)  // ms, how often we read & integrate the flow meter, should be below 25 ms
#define OXYGEN_INTERVAL 4     // After the oxygen sensor is triggered, then next Nth time it is read, because there needs to be 100 ms between trigger & read

// Time to integrate the oxygen consumption volume (1 minute)
static int INTEGRATION_TIME = 15000;  // Update every 15 seconds by default
#define NORMALIZATION_TIME  60000     // ms, normalize to this value, e.g. normalize to 60 seconds (e.g. veMean = liters / 1 minute)
static unsigned int STORE_RATE = 0;   // How often store the values to buffer, default=every integration step

static uint16_t errorCounter = 0;

// Struct where sensor data is be copied on command
sensorData_t sensorData;

// Structure where data is buffered
storeData_t bufferData[STORE_BUFFER_SIZE] = {0};
uint16_t bufferPosition = 0;

typedef enum {
  IDLE = 0,
  READ_FLOW,      // Read & integrate flow in the venturi tube
  READ_O2,        // Read exhaust O2 sensor
  READ_CO2,       // Read exhaust CO2 sensor
  READ_PRESSURE,  // Read ambient pressure (& temperature)
  CALC_AIRDENSITY,  // Calculate air density
  CALC_VOLUMES,      // Calculate volume
} sensorSequence_t;

// Here we define in what order the sensors are read
// First item is read between all other items also
static sensorSequence_t sequence[] = {
  READ_FLOW,          // At 400 kHz this takes currently 240 us
  READ_O2,
  READ_CO2,
  READ_PRESSURE,      // At 100 kHz currently takes 940 us. 400 kHz --> 310 us (calculation takes almost no time)
  CALC_AIRDENSITY,
  CALC_VOLUMES,
};

static const uint8_t sequenceSteps = sizeof(sequence) / sizeof(sensorSequence_t);

static const float calculationRate = ((2 * sequenceSteps) - 2) * READINTERVAL;  // How often (in ms) we calculate everything
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

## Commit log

2024-09-01 Create PCBAs README.md
2024-09-01 Add gerber files for the Sensirion SDP801 PCB
    [sensirion-Edge_Cuts.gbr, sensirion-F_Cu.gbr, sensirion.drl]
2024-09-01 Add the main 3D model step file
    [Main model v12.step]
2024-09-01 Add the cover 3D model step file
    [Cover v12.step]
2024-09-01 Add the mask holder 3D step file
    [Mask holder v10.step]
2024-09-01 Add inlet valve 3D model files
    [Inlet valve v3 26mm membrane holder.stl, Inlet valve v3 26mm template.stl, Inlet valve v4 26mm body.stl, Inlet valve v4 26mm retainer.stl]
2024-09-01 Add outlet valve 3D models
    [Outlet valve v1 30mm template.stl, Outlet valve v2 30mm body.stl, Outlet valve v2 30mm membrane holder.stl]
2024-09-01 Add picture of preferred print orientations
2024-11-06 Update libraries, add recording feature+bugfixes
    New versions of libraries:
    - ESP32 for arduino by espressif 3.0.5
    - TFT_eSPI 2.5.43
    - NimBLE_Arduino 1.4.1
    Fixes:
    - Fixes to I2C timeouts, maybe regression because of new library versions.
    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
2024-11-08 Small enhancements
    Some enhancements:
    - Add menu test element to change Wifi name and password
    - Replace hardcoded device ID with tow last bytes of ESP32 MAC address
    - Zero some calculated values if no breathing during integration period
    - Change and add quantities that are stored in memory buffer
2025-08-13 Storage memory can now be stored to flash
    Storage memory can be saved to a flash file from the menu and later (e.g. after power down) be sent over wifi to computer for further analysis.
2025-08-18 Reset flow correction factor before calibration
    Flow correction factor must be reset to 1.0 before flow calibration, as the calibration must be done without the correction...
2025-08-20 Clean up some text in flow calibration
2025-08-21 Add some debug outputs to sensor task
2025-08-21 Correct sensor data sutrcture description
    Wrong units in sensordata description compared to the code
2025-08-22 Try to fix battery voltage reading
    Apply theoretically correct gains to battery voltage reading as it is currently way off
2025-08-22 Custom scaling for battery ADC values
    Custom linear scaling from ADC to battery voltage. The ADC reading has at least 160 mV offset (96 mV in positive terminal and 66 in negative) and the gain of the ADC preamp is way off. Also USB volta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
2025-08-22 Update battery voltage display and color levels
    Should display battery status better now, and indicate whether close to getting issues...
2025-08-22 Add co2 concentration to sensor data buffer
2025-08-22 Comment out battery debug logging
